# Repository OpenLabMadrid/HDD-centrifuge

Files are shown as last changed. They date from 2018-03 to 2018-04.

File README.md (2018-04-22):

# HDD centrifuge

The design of this machine have been made by OpenLab Madrid, *getting the initial idea* in the *hackteria wiki* (https://hackteria.org/wiki/Hacked_Hard-disc_Centrifuge) and adding some changes to adapt the machine to our needs.
## Electronics

For the detailed descriptions and links to the components that we have buy see the Bill Of Materials (BOM) file in the "Electronics" folder.

### Power supply

For the power supply we are using an Aliexpress 12V 3A one. Less than 3A may be insufficient for this centrifuge.

### Understanding the electronic components
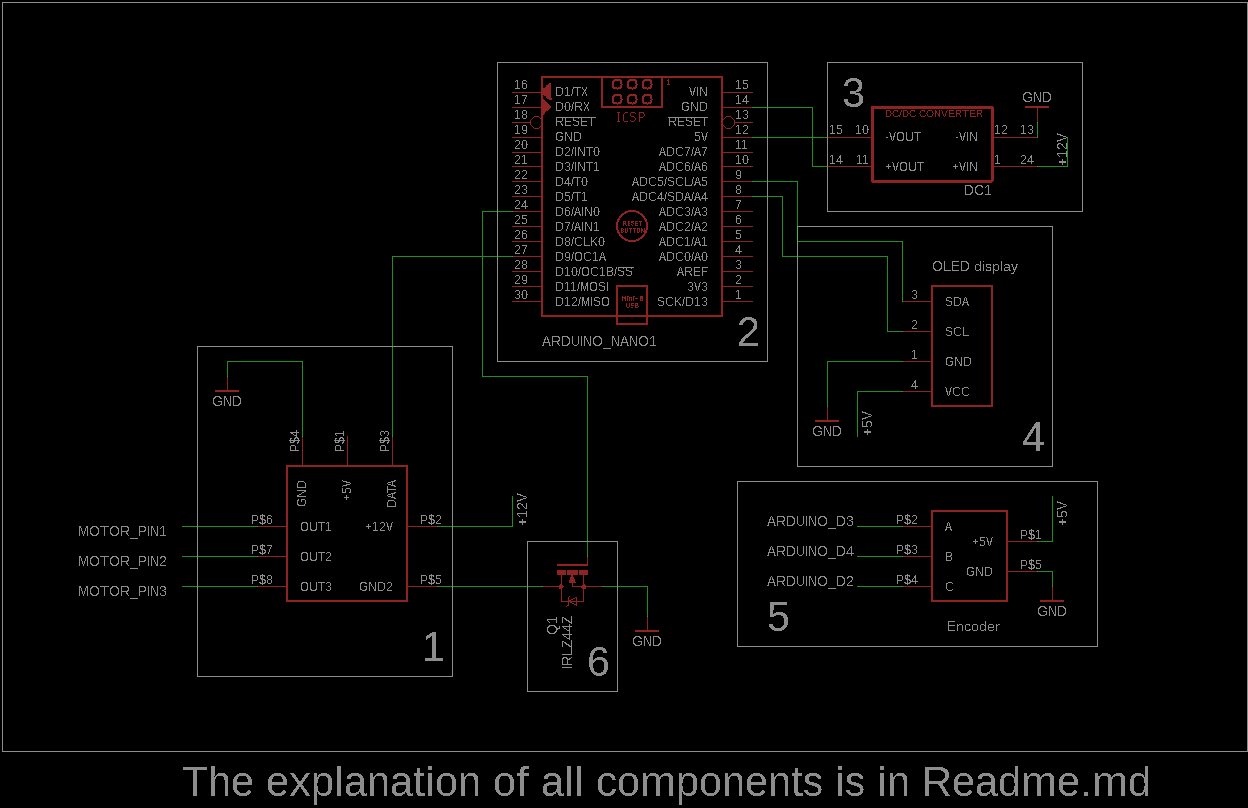
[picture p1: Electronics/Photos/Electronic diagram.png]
Electronic diagram


_Part 1: Esc controller_. This is the driver of the HDD Brushless motor. It send a triphasic PWM signal over 3 pins of the motor. The problem is that motors use to have 4 pins. You need to found the 3 pins attached to the 3 inductors of the motor and "discard" the pin associated to the common ground of them. To made this, you will need a polimeter to measure the resistances between the different pins. The pins of the three inductors will have the same resistance between them and the ground. You will need to keep measuring the resistance until you found the pin with which the other 3 have the same resistance. This is the ground, the other 3 must be the inductor pins. Connect them to the ESC controller.



_Part 2: Arduino nano_. For mounting all the electronic chips, we have been using perforated PCBs but we are planning to migrate to printed PCB to save the huge time used soldering the wires. The Arduino nano is the main controller. We are using the chinese clone (from Aliexpress, Banggood,...) with the TTL CH340 chip which needs a special driver to program it from the PC. You could find easily on google searching for "CH340 arduino driver".

The pins that we are using are:
- LCD
	- SDA: pin A4
	- SCL: pin A5
	- GND: Arduino GND
	- VCC: Arduino +5 V
- Encoder
	- Encoder output A: pin D3
	- Encoder output B: pin D4
	- Encoder button output: pin D2
- ESC
	- ESC digital control: pin D9
	- Enable ESC: pin D6

_Part 3: DC-DC converter_. This converter transform the alimentation provided by the power supply (12V) to the voltage that arduino needs (5V). Arduino have a built-in dc-dc converter that can manage 12V but this is the upper limit of the converter, and because the voltage of the power supply could vary a bit, this is the way to protect the Arduino. This converter also have capacitors to stabilize the power supply noise, that will be good for our project.

_Part 4: LCD_. We are using a 0.96" OLED which provide 128x64 pixel resolution. The advantages are that it´s cheap, it only uses 2 pins apart of the alimentation ones and you can draw graphics, logos and elegant menus on it.

_Part 5: Encoder_. Is the best way we hava found to introduce the orders in the centrifuge. You can learn a lot of this sistems with a simple search on google like "Arduino Encoders".  

### The result

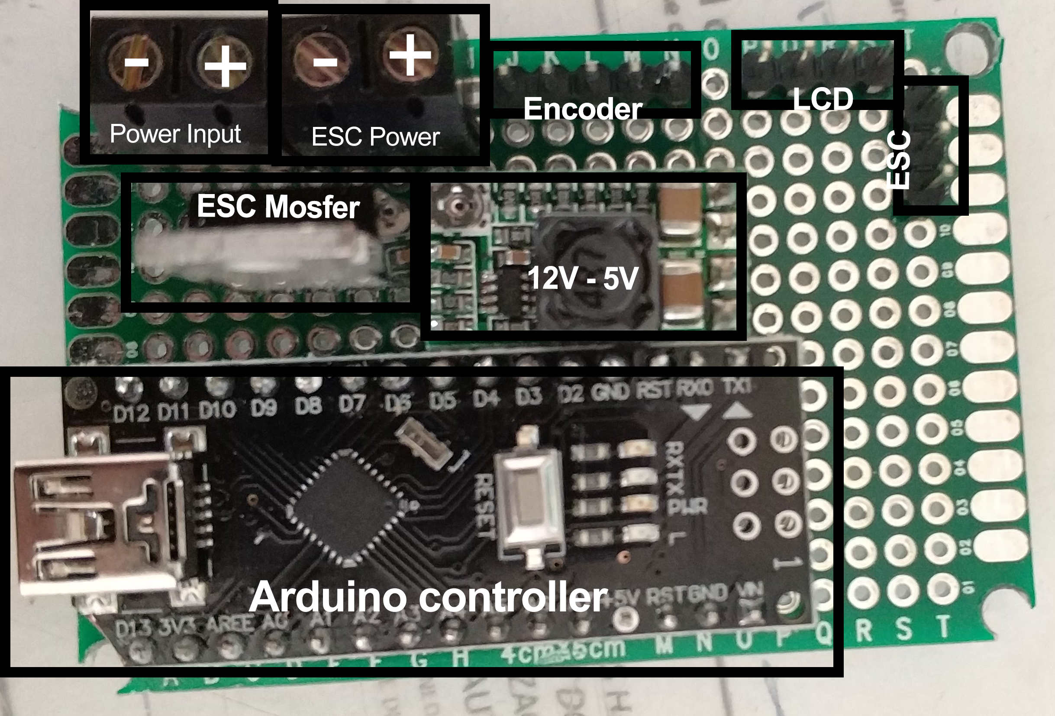
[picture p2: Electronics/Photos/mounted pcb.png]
PCB


To solder the components between eachothers we are using awg30 wire:

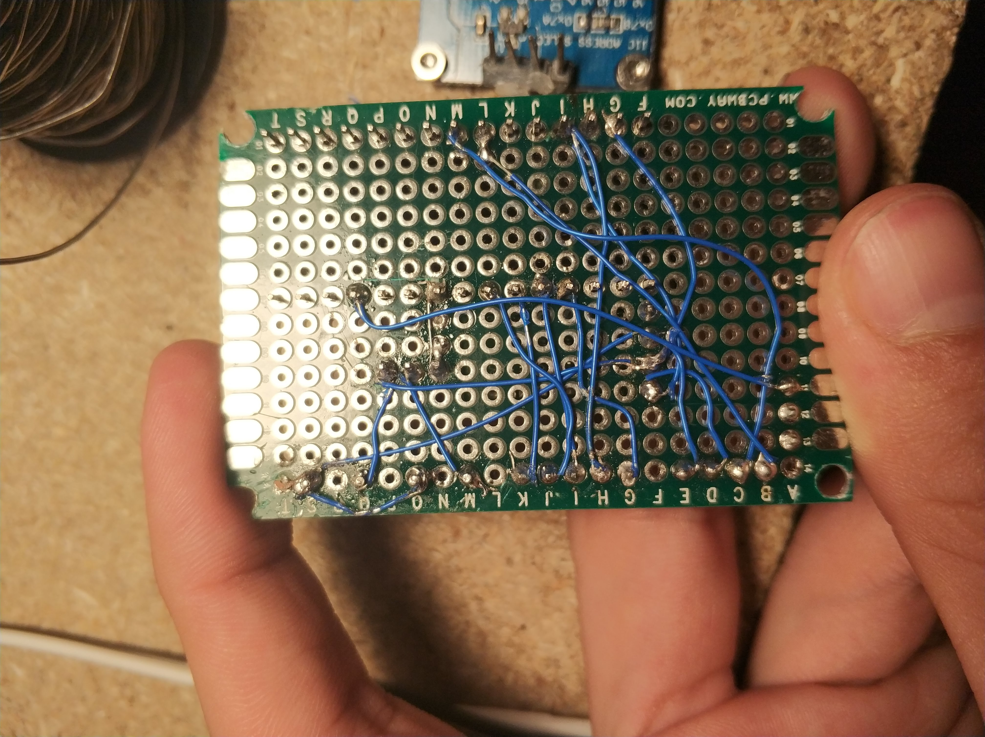
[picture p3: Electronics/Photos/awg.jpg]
awg pcb


## Making the solid parts (case and rotor)
### Step 1: Case
The case files are in the "Laserable and 3D printable" folder. Here, you will find the SolidWorks assembly files of all the parts you will need and the .dxf files to cut in a laser cutter machine. If you don´t have the SolidWorks software don´t worry, we have attached a .jpg capture of all the case mounted in the "Images of the mounted device" folder: 

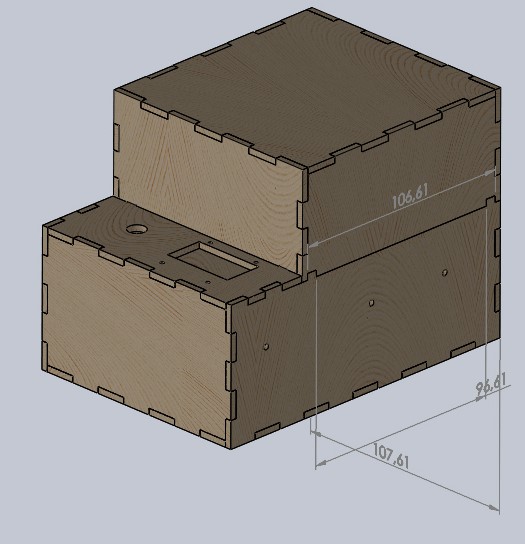
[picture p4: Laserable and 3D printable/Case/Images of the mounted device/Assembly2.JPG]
Assembembly example 2


The material must be 3mm thickness and we have used MDF for the HDD enclosing and transparent acrylic for the cover. The MDF have been stuck with white glue and the acrylic with cloroform or 
cyanoacrylate (better the first one).  

### Step 2: Rotor
You can find the .stl file in the "Laserable and 3D printable" folder. We have printed it in PLA, 0.2mm thickness and 20% infill without supports.

It is true that the result of the 3D printer is not perfectly symmetrical and in the case that we are managing more g forces, it will be dangerous to install this rotor in a centrifuge, but with which we are managing, you won´t have problems. A more symmetrical rotor made from acrilic and laser cutting machine, could be found in the Hackteria wiki.   

## Installing the code
### Step 1: Installing the libraries
Download the u8glib library (The folder called ug8lib inside the one called Arduino Code) and install it following the normal process (https://www.arduino.cc/en/Guide/Libraries) or copy it to "\Documents\Arduino\libraries" path.
### Step 2: Burn the code in your Arduino
You must select Arduino nano as board, ATMEGA328 as processor, and the port in which the arduino is connected.

If the port is not listed, make sure that you have installed the drivers from the chinese clone of Arduino about which we have been speaken in the previous steps.

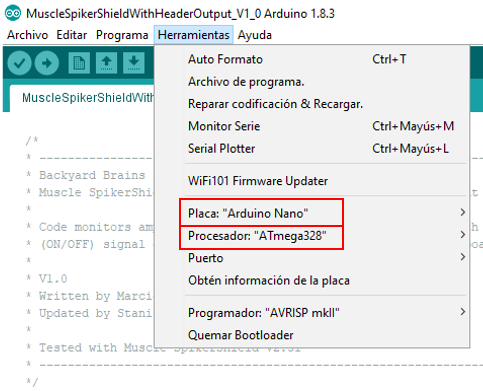
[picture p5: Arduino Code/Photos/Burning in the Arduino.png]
Burning in the Arduino


And enjoy it!

## Support
Any question could be made sending an email to info@openlabmadrid.es, feel free to ask anything.

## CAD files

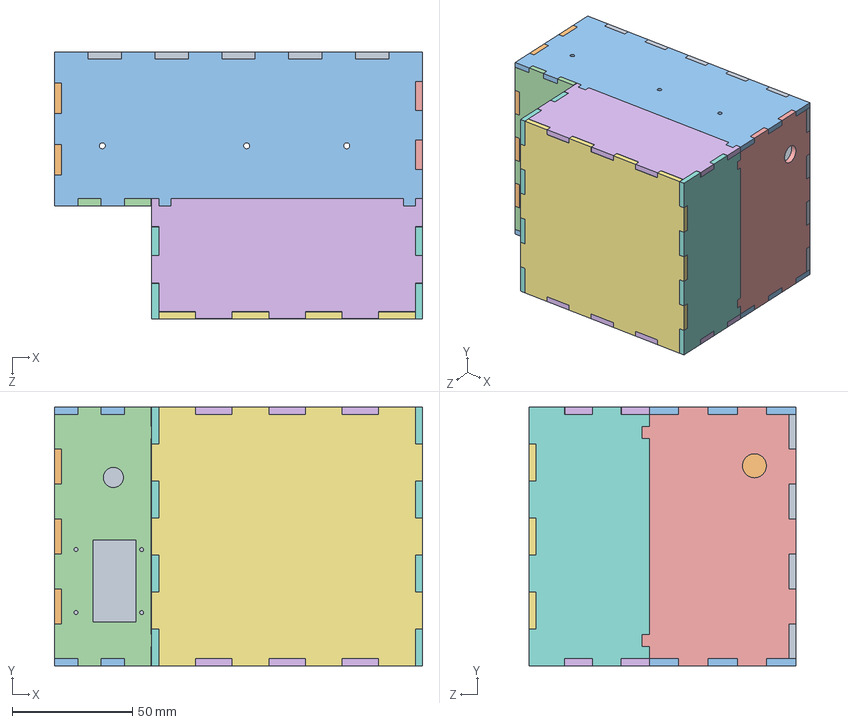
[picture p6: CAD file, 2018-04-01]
Laserable and 3D printable/Case/SolidWorks design files/Ensamblaje1.SLDASM
153.0 x 107.6 x 111.0 mm
FondoHDD2
DelanteroHDD2
LateralHDD2 x 2
TopHDD2
TraseroHDD2
TapaLateral x 2
Tapatop
TapaTrasero x 2

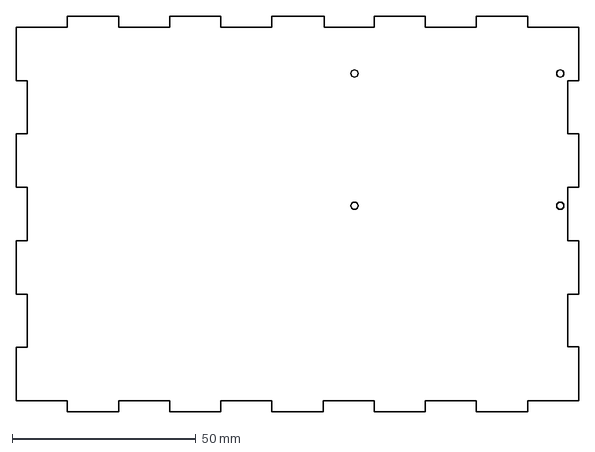
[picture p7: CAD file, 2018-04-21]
Laserable and 3D printable/Case/.dxf
153.0 x 107.6 mm

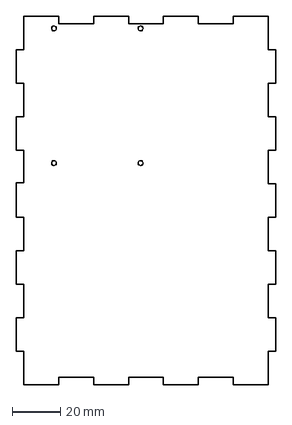
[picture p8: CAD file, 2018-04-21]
Laserable and 3D printable/Case/.dxf files/FondoHDD2.DXF
107.6 x 153.0 mm

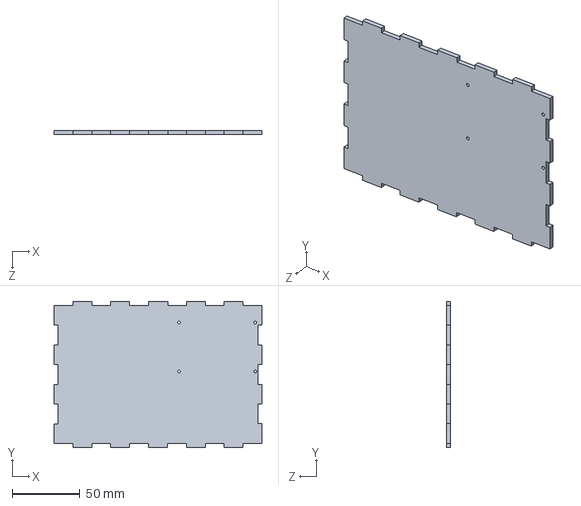
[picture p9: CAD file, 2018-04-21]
Laserable and 3D printable/Case/SolidWorks design files/FondoHDD2.SLDPRT
153.0 x 107.6 x 3.00 mm

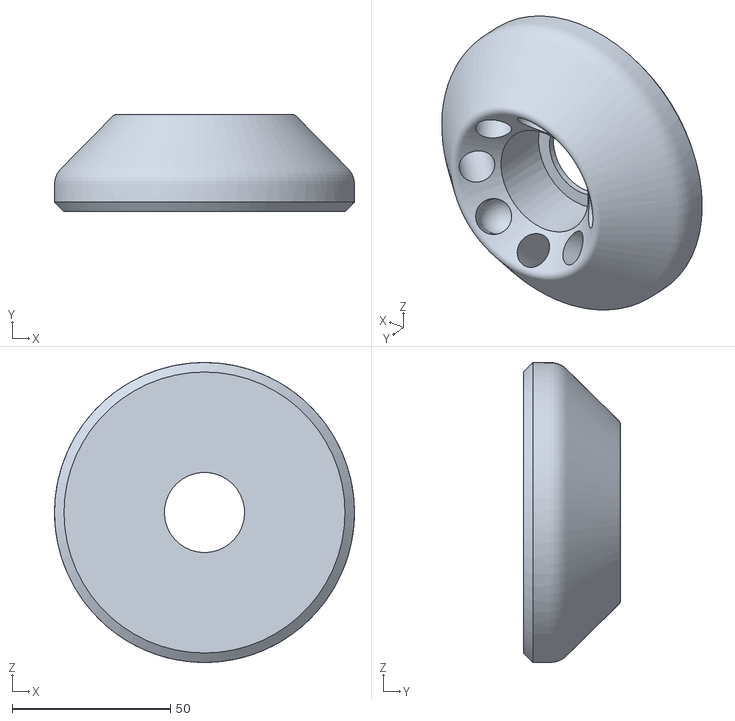
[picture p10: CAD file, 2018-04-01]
Laserable and 3D printable/Rotor/Rotor.STL
94.7 x 30.7 x 94.7

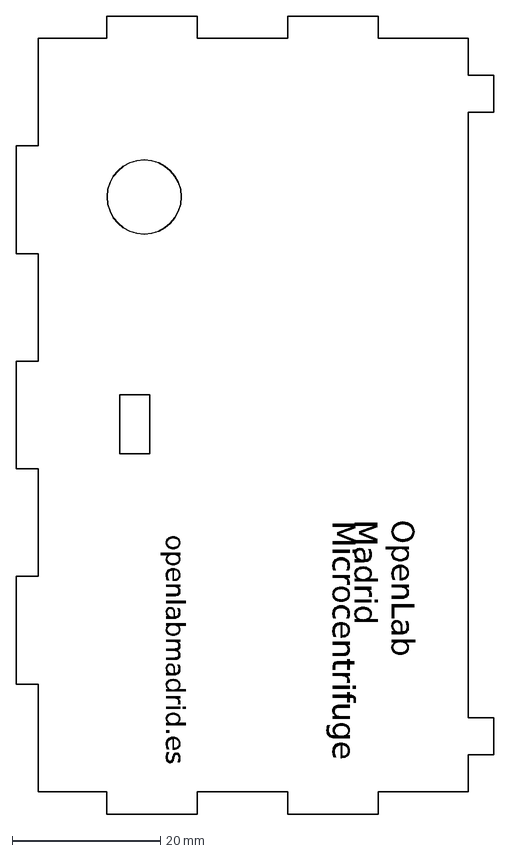
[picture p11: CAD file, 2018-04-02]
Laserable and 3D printable/Case/.dxf files/TraseroHDD2-USB.DXF
openlabmadrid.es
Microcentrifuge
OpenLab Madrid

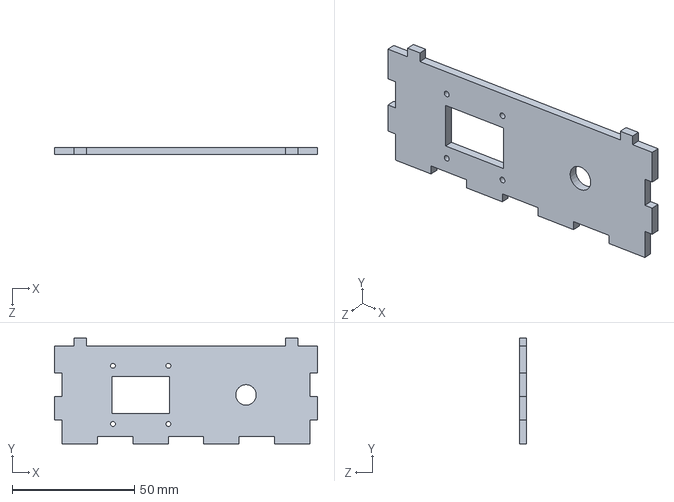
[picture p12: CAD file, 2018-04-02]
Laserable and 3D printable/Case/SolidWorks design files/TopHDD2.SLDPRT
107.6 x 43.2 x 3.00 mm

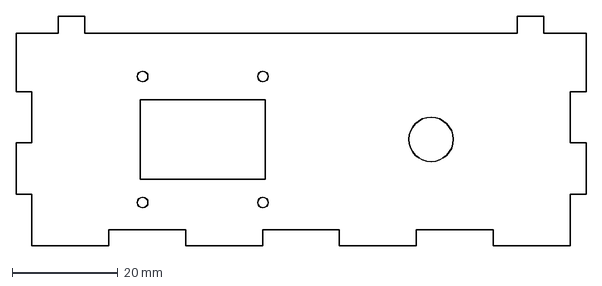
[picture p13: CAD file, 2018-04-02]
Laserable and 3D printable/Case/.dxf files/Top-HDD2.dxf
107.6 x 43.2 mm

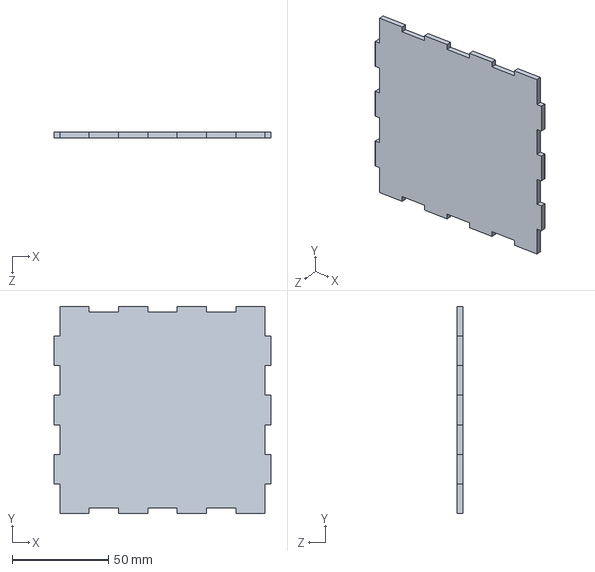
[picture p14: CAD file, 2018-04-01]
Laserable and 3D printable/Case/SolidWorks design files/Tapatop.SLDPRT
112.6 x 107.6 x 3.00 mm

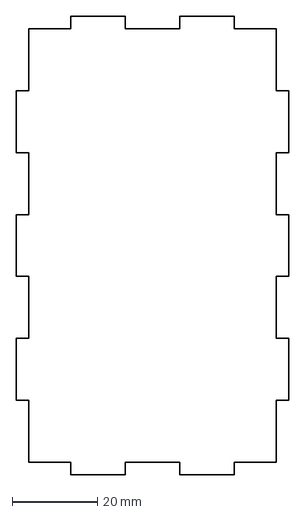
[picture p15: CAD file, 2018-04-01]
Laserable and 3D printable/Case/.dxf files/DelanteroHDD2.DXF
64.0 x 107.6 mm

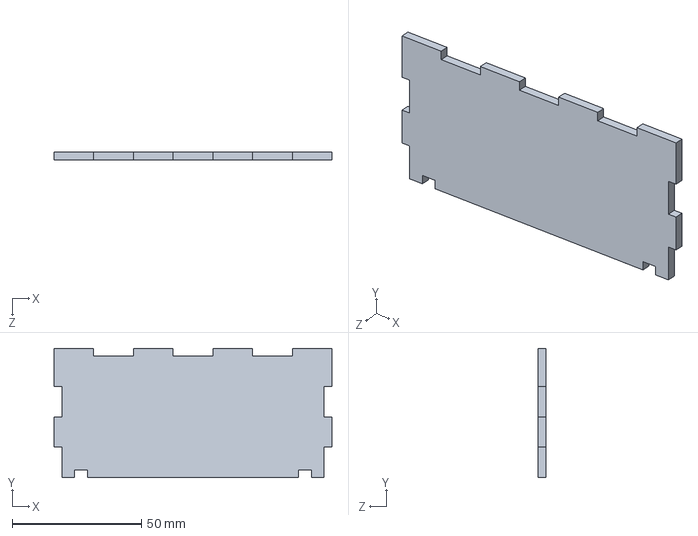
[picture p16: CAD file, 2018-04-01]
Laserable and 3D printable/Case/SolidWorks design files/TapaTrasero.SLDPRT
107.6 x 50.0 x 3.00 mm

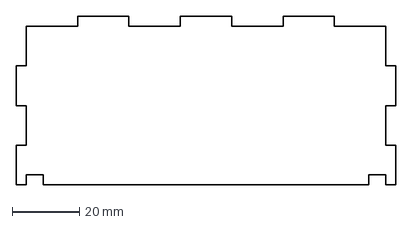
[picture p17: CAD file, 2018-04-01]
Laserable and 3D printable/Case/.dxf files/TapaLateral.DXF
112.6 x 50.0 mm

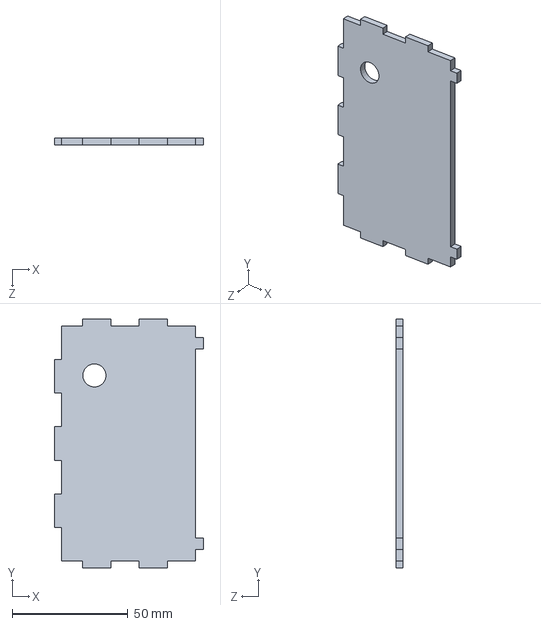
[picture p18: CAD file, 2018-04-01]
Laserable and 3D printable/Case/SolidWorks design files/TraseroHDD2.SLDPRT
64.4 x 107.6 x 3.00 mm

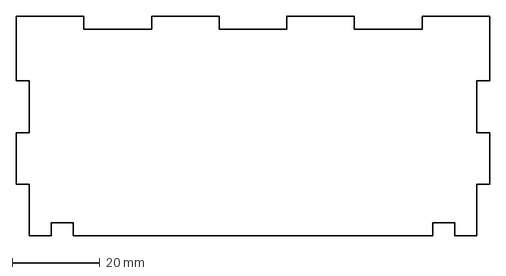
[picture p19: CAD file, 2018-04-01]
Laserable and 3D printable/Case/.dxf files/TapaTrasero.DXF
107.6 x 50.0 mm

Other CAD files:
Laserable and 3D printable/Case/SolidWorks design files/LateralHDD2.SLDPRT
Laserable and 3D printable/Case/.dxf files/Tapatop.DXF
Laserable and 3D printable/Case/SolidWorks design files/DelanteroHDD2.SLDPRT
Laserable and 3D printable/Case/.dxf files/TraseroHDD2.DXF
Laserable and 3D printable/Case/.dxf files/LateralHDD2.DXF
Laserable and 3D printable/Case/SolidWorks design files/TapaLateral.SLDPRT

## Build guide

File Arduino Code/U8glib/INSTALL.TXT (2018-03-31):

U8GLIB
http://code.google.com/p/u8glib/

Install instructions for the Arduino environment.

  1. Start Arduino IDE
  2. In the Arduino IDE, import the library from the "Add Library" Menu.

Alternative install instructions for the Arduino environment.

  1. Unzip u8glib_arduino_vX.XX.zip into the "libraries" folder of the
      Arduino install directory
  2. Start Arduino IDE

Install instructions for the Chipkit (Arduino) environment.

  1. cd <mpide-... path>/libraries
  2. unzip u8glib_arduino_vX.XX.zip
  3. cd <mpide-... path>///hardware/pic32/libraries
  4. again: u8glib_arduino_vX.XX.zip
  5. Open hardware/pic32/cores/pic32/Print.h
	  Remove line
	    #define BYTE 0
	  from the file, use PRINT_BYTE instead of BYTE.

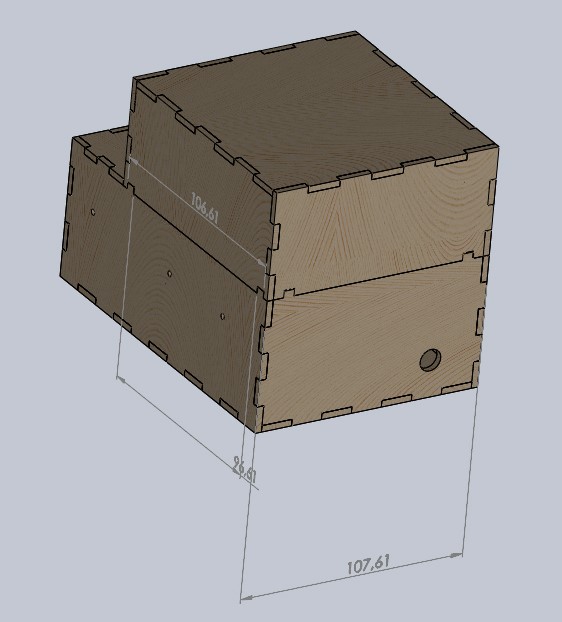
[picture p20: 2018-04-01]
Laserable and 3D printable/Case/Images of the mounted device/Assembly1.JPG

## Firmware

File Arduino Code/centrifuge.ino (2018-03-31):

// include the necessary libraries
#include <SPI.h>
#include <SD.h>
#include "U8glib.h"
#include <Servo.h>


//pin defines
#define lcd_cs 10
#define dc     8
#define rst    7
#define encA 3 //Enconder output A
#define encB 4 //Enconder output B
#define encC 2 //Enconder button output
#define ESCpin 9  //Pin for ESC control
#define E_ESC 6 //ESC enable

#define TIMER2ON  TIMSK2=(0<<7)|(0<<6)|(0<<5)|(0<<4)|(0<<3)|(0<<OCIE2B)|(0<<OCIE2A)|(1<<TOIE2)
#define TIMER2OFF TIMSK2=(0<<7)|(0<<6)|(0<<5)|(0<<4)|(0<<3)|(0<<OCIE2B)|(0<<OCIE2A)|(0<<TOIE2)


///////////Functions//////////
//interruption functions
int pressed ();
int moved ();
ISR(TIMER2_OVF_vect);

//general functions
void manageLastPress();
bool EncoderDirection ();
void startRotor (int rpm, unsigned int _min); 
void pauseRotor();
void DrawMenu(int _menu);
void spin();

//initialization function
void initialize ();

/////Variable initialization/////

//Time control
unsigned int counter = 0;

//Velocity control
int rpm = 2000;
unsigned int _min = 1;
unsigned int sec = 0;

//ESC
Servo ESC; 

//Screen
U8GLIB_SH1106_128X64 u8g(U8G_I2C_OPT_NONE);

//encoder
int aState;
int aLastState;
int pulsado;
int movido = 100;
int lastPress;
bool WasPressed = false;

//Menu
int selection=0;
int TimeRunning = 0;

void setup() {
  initialize();

}

void loop() {
  if (WasPressed)
    manageLastPress();

  
}

////////////////////////////////////////Functions defenition//////////////////////////////////////////

/////////////////////////////////Interruption Functions/////////////////////////

int pressed ()
{
  if (millis()-lastPress > 500)
  { 
    WasPressed = true;
    lastPress = millis();
  }
}
int moved ()
{
  if (millis()-lastPress > 50)
  {
    switch (selection){
      case 0:
        if (EncoderDirection() && rpm < 7200)
        {
          rpm += 100;
          DrawMenu(0);
        } else {
          if ( rpm > 0)
          {
            rpm -=100;
            DrawMenu(0);
          }
        }
      break;
      case 1:
        if (EncoderDirection() && _min < 1000)
        {
          _min += 1;
          DrawMenu(1);
        } else {
           if (_min > 1)
           {
            _min -= 1;
            DrawMenu(1);
           }
        }
    }
    lastPress = millis();
  }
}

ISR(TIMER2_OVF_vect){
  counter++; 
  if (counter > 3676)
  {
    if(_min!=1)
    {
      _min--;
      counter = 0;
      DrawMenu(2);
    } else {
      counter = 0;
      selection = 0;
      DrawMenu(0);
      pauseRotor();
      TIMER2OFF;
    }
  }
}
///////////////////////////////////General functions//////////////////////////////
void manageLastPress()
{
    int state;

    delay(500);
    
    state = digitalRead(2);
    
    if( (state == 0) && (selection == 0 || selection == 1))
    {
      if (selection == 0) //Spin
        spin();
      if (selection == 1) //Return to main Menu
      {
        selection = 0;
        DrawMenu(0); 
      }
    } else {   
      switch (selection)
      {
        case 0:
          DrawMenu(1);
          selection = 1;
        break;
        case 1:
          TIMER2ON;
          DrawMenu(2);
          selection = 2;
          startRotor(rpm, _min);
        break;
        case 2:
          pauseRotor();
          selection = 0;
          DrawMenu(0);
        break;
      }
    }
    WasPressed=false;
}
bool EncoderDirection () //TRUE formward FALSE backward
{
    if (digitalRead(encB) == LOW)
    {
      return true;  //Moved forward
    } else {
      return false; //Moved backward
    }
}


void startRotor (int rpm, unsigned int min)
{
  int objetive = map(rpm,0,7200,700,2000);
  for (int i = 700; i<objetive; i+=100)
  {
    ESC.writeMicroseconds(i);
    delay(500);
  }
  ESC.writeMicroseconds(objetive);
}

void pauseRotor()
{
  ESC.writeMicroseconds(700);
}

void DrawMenu (int _menu)
{
  switch (_menu)
  {
    case (0):
      u8g.firstPage();  
      do {
          u8g.setFont(u8g_font_unifont);
          u8g.drawStr( 0, 22, String(String(rpm) + " rpm").c_str());
          u8g.setFont(u8g_font_6x10);
          u8g.drawStr( 0, 40, "Press to enter time");
          u8g.drawStr( 0, 52, "Hold for spin");
      } while( u8g.nextPage() );
      break;
    case(1):
        u8g.firstPage();
       do {
          u8g.setFont(u8g_font_unifont);
          u8g.drawStr( 0, 22, String("Minuts: " + String(_min)).c_str());
          u8g.setFont(u8g_font_6x10);
          u8g.drawStr( 0, 40, "Press to start");
          u8g.drawStr( 0, 52, "Hold for cancel");
      } while( u8g.nextPage() );
      break;
    case(2):
      u8g.firstPage();
          do {
            u8g.setFont(u8g_font_unifont);
            u8g.drawStr( 0, 22, "RUNNING");
            u8g.drawStr( 0, 42, String(String(_min)+" mins left").c_str());
            u8g.setFont(u8g_font_6x10);
            u8g.drawStr( 0, 52, "Press to cancel");
          } while( u8g.nextPage() );  
      break;
  }
}

void spin ()
{
    int objetive = map(rpm,0,7200,700,2000);
    int i;
    while (digitalRead(2) == LOW)
    {
      if (i < objetive)
      {
        i += 100;
        ESC.writeMicroseconds(i);
      } else {
        ESC.writeMicroseconds(objetive);
      }
    }
}
////////////////////////////////////Initialization Function////////////////////////
void initialize ()
{
  Serial.begin(9600);


  ///////////////////////////Pin Initialization//////////////////////////////////
  //encoder
  pinMode (encA,INPUT);
  pinMode (encB,INPUT);
  pinMode(2, INPUT_PULLUP);
  //ESC
  pinMode(E_ESC, OUTPUT); 
  ///////////////////////////////////////////////////////////////////////////////

  u8g.firstPage();
       do {
          u8g.setFont(u8g_font_unifont);
          u8g.drawStr( 0, 40, "Initializing...");
      } while( u8g.nextPage() );

  //////////////////////////////////ESC controller initialization//////////////// 
  //activate the MOSFET wich enable the ESC 
  digitalWrite (E_ESC, HIGH);

  delay(500);
  //ESC initialization sequence
  while (!ESC.attached())
  {
  ESC.attach(ESCpin);   
  delay(200);
  } 
  ESC.writeMicroseconds(2000); 
  delay(2000);
  ESC.writeMicroseconds(700); 
  delay(2000);
  ////////////////////////////////////////////////////////////////////////////////

  /////////////////////////////////////Timer 2/////////////////////////////////////
    //Activación y preparación de la interrupcion del TIMER2 para que funcione a 1 Hz (una vez por segundo)
  TCCR2A = (1<<COM2A1) | (0<<COM2A0) | (0<<COM2B1)| (0<<COM2B0) | (0<<3) | (0<<2) | (0<<WGM21) | (0<<WGM20);  ;   //modo normal, sin pwm, sin cuenta
  TCCR2B = (0<<FOC2A) | (0<<FOC2B) | (0<<5) | (0<<4) | (0<<WGM22) | (1<<CS22) | (1<<CS21) | (1<<CS20);
  TIMSK2 &= ~(1<<OCIE2A); //quitamos comparación, solo queremos por overflow
  // Oscilador interno
  ASSR = (0<<7) | (0<<EXCLK) | (0<<AS2) | (0<<TCN2UB) | (0<<OCR2AUB) | (0<<OCR2BUB) | (0<<TCR2AUB) | (0<<TCR2BUB) ;
  // configuramos un prescaler de 1024
  TCCR2B |= (1 << CS22) | (1 << CS21) | (1 << CS20);
  ////////////////////////////////////////////////////////////////////////////////
    
  //////////////////The start/////////////////
  DrawMenu(0);
  EIFR  = bit (INTF0); // clearing button pushed before the menu drawing
  
  /////////////////////////Interruptions initialization///////////////////////////
  attachInterrupt(digitalPinToInterrupt(2), pressed,FALLING); //enconder have been pressed
  attachInterrupt(digitalPinToInterrupt(3), moved,LOW); //enconder have been rotated
  ////////////////////////////////////////////////////////////////////////////////

}

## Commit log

2018-03-31 Arduino code + library
2018-04-01 laserables and printables, readme.md modifications
    [DelanteroHDD2.DXF, DelanteroHDD2.SLDPRT, Ensamblaje1.SLDASM, FondoHDD2.DXF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]
2018-04-02 readme, schematics, laserables 2.0
    [.dxf, Top-HDD2.dxf, TopHDD2.DXF, TopHDD2.SLDPRT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]
2018-04-21 Trying images in readme.md
    [.dxf, FondoHDD2.DXF, FondoHDD2.SLDPRT]
2018-04-22 Photo to demonstrate the arduino code burn
